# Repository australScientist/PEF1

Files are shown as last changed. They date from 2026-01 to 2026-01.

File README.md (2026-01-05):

# The Ecophysiometer: An Open-Source Multipurpose Environmental Sensor

The **Ecophysiometer** is a low-cost (\~US\$128), modular environmental monitoring platform designed to acquire rich optical data and interpret it through chemometric calibration. Developed at the Universidad Nacional de Córdoba (UNC), CONICET and the Technical University of Rheinland-Pfalz, Landau (RPTU) this project shifts analytical complexity from hardware to software, enabling multi-analyte quantification with flexible, 3D-printable instrumentation.

## 📁 Repository Structure

The project is organized to support both hardware fabrication and data analysis:

```         
/Design/Hardware: Engineering files for the flow cell, modular housing, and sensor mounts in FreeCAD and STL formats. Includes KiCAD project files for the constant-current PCB.
```

/Design/Software: Python source code including the core Measurement.py, ImageProcessor.py, and SpectralData.py layers .

/Instructions: Step-by-step assembly guides, including the critical IR filter removal tutorial for the Raspberry Pi Camera .

/Characterisation: Raw data and R scripts used to validate signal stability, linear range, and manufacturing variability.

/Implementation examples: Datasets and R models for the primary use cases: Turbidity and Phytoplankton differential quantification.

## 🛠️ Key Technical Features

```         
Software-Defined Specificity: Analyte detection is determined by chemometric calibration (PLSR, PCA) rather than fixed hardware filters.
```

High-Certainty Signal Processing: The pipeline aligns 450 vertical rows and applies 5-pixel binning, deriving each data point from the average of 2,250 measurements to maximize the signal-to-noise ratio .

Reproducible Hardware: Designed for manufacturing with minimal technical knowledge using locally available electronic materials and 3D printing in PETG .

## 🚀 Getting Started

### 1. Hardware Fabrication

```         
3D Printing: Print parts found in /Design/Hardware. Black PETG is recommended to minimize internal reflections.
```

[Circuitry]{.underline}: Fabricate the PCB using the provided KiCAD files or the CNC-ready .nc files in the Circuit Board directory.

[Sensor Modification]{.underline}: Follow Instructions/IR_REMOVAL.md to remove the IR cut-off filter from the Raspberry Pi Camera V1.3.

### 2. Software Installation

Clone this repository and install the dependencies: Bash

git clone <https://github.com/australScientist/PEF1.git> cd PEF1 pip install -r Design/Software/PEF0/requirements.txt

### 3. Basic Operation

[Calibration]{.underline}: Run test.py to identify the linear integration time for your specific hardware assembly .

[Measurement]{.underline}: Launch the graphical interface: Bash

```         
python3 Design/Software/PEF0/src/GUI2.py
```

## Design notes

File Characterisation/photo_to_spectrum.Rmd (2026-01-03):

---
title: "photo_to_spectrum"
author: "Guido Marconi"
date: "`r Sys.Date()`"
output: html_document
---

```{r Rsetup, include=FALSE}
knitr::opts_chunk$set(echo = TRUE)
library(reticulate)
renv::use_python()
library(tidyverse)
library(gganimate)
```

```{python PySetup, include=FALSE}
#import matplotlib as mpl
import numpy as np
#import matplotlib.pyplot as plt
from scipy.signal import correlate
import rawpy
import os
```

## Intro

The goal of the instrument is to measure light intensities at different wavelengths. To achieve this two simple concepts are used. The first is that diffraction can be used to produce a spatial separation of light into its spectral components. The second is that the intensity of each component of light can be then recovered by an array of sensors with capacity for spatial resolution, such as a camera. The problem begins with the oversimplification of considering cameras just as an array of sensors and continues with a fundamental misconseption about what their design goals were. Cameras are devices designed to capture images that are comparable to the human visual system. As trivial as this statement seems, it contains the information needed to structure the process of adapting a camera to suit our goal. 

Fundamentally the root cause of the problem to be solved is that light as perceived by humans is not exactly the same as light as physical phenomenon. Humans experiment light as colour, and cameras (and the post-post processing of the photos) aim at replicating this perceptual phenomenon. Thus, a photograph is composed of patterns of colour at different points of space, not "just light".

Briefly, colour is a physiological response to light and, according to the CIE 1931, its the product of the stimulation of three types of cone cells. This gives rise to the idea of colour as a response to tristimulus values and to the representation of colour as a space defined by three axis. Perhaps the most intuitive representation of this is the RGB colour space defined by the amount of light at each of Red, Green and Blue "primary" colours. A generalization of this is that colour, as perceived by humans, can be decomposed into three parts parts: one regarding the illuminance of the colour and the remaining two describing its chrominance. Making this distinction is important because, for analytical purposes, the illuminance aspect of the signal is the only relevant component but when the signal is recovered from the camera it is convoluted with all the other aspects that make the image have colour.

Leaving behind all the optical elements, cameras can be thought as having two components. A sensitive component aimed at measuring the illuminance part of colour and another part aimed at obtaining chromatic information. Briefly, the sensors translate photon counts into a voltage difference that gets amplified and red. The working principle is the photoelectric effect. Basically, pixels work as capacitors that hold charge generated when photons excite electrons until they it is red, resetting the pixel for the next measurement. This is enough to represent the luminance aspect of colour, but not the chrominance. To overcome this and produce a tricromatic image, each pixel in the sensor is coated with a filter for red, green and blue light, conforming a colour filters array (CFA). This CFA restricts each pixel to capture information only about the intensity of light that was not absorbed by the filter on top of it. Thus the pixel values in the raw image represent the amount of light only in one primary component of light (either blue, green or red). 

To solve this issue post processing of the image interpolates the values of the remaining components to achieve a full colour representation of each pixel. There are several interpolation algorithms that can be used, each with its advantages and disadvantages and will be analized in a future section. Another situation to take into account is that human perception of brightness is not linear, it follows a power function. To emulate this, comonly post processing uses a gamma correction that translates the quasi linear response of the instrument into a power distribution. Lastly, when the luminance component is obtained from the full colour value of each pixel, it is usually a ponderated sum of the R, G and B components taking into account our sensitivity to each of these colours. 

Here we face the first set of problems or warnings that need to be addressed:

- Filters restrict the amount of photons that get sensed to three bandwidths. This has two practical implications:

  - The measurement of the luminance is composed from the the true colour representation of each pixel, which in turn is an interpolation from the observed RGB values.
  
  - There is a limitation in the bandwidth.

- The mechanism used to obtain the chrominance components of the colour is rooted into the spatial disposition of pixels. This is something to take into account because the spectra is already spatially separated.

- The gamma correction has to be set as a power of one and with a slope of one so that the response in the R, G and B components is linear.

- A gray-scale or luminance is a pondered average of RGB components such that the result represents 

The camera is based on the OmniVision [OV5647 sensor]("https://cdn.sparkfun.com/datasheets/Dev/RaspberryPi/ov5647_full.pdf"). It is a CMOS an sensor array of 2624 columns to 1965 rows, with a pixel dimension of 1.4 µm × 1.4 µm and a total sensor area of 3.76 × 2.74 mm.

## Working with the Raw image

### Script to process the photo

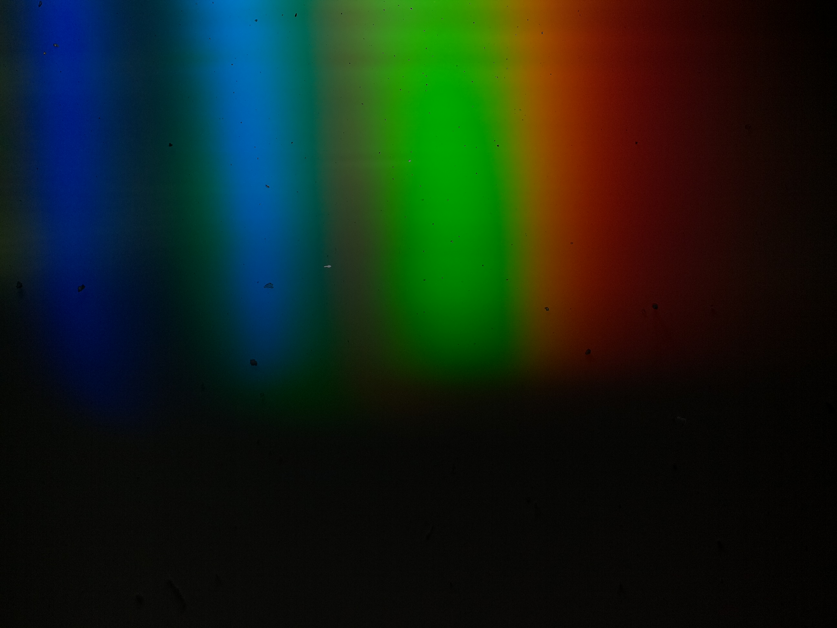
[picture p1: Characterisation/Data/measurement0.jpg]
Raw output Sensor output
Concretely, the output of the camera looks something like this: . Visual inspection already allow us to identify some behaviours that should reflect on the final result (spectra):

+ The shortest wavelengths (blue) of the spectra are present at the left part of the picture while the longer wavelengths (red) are at the rightmost part.

+ The intensity of the spectra is not uniform. It has bands of higher and valleys of lower intensity.

+ The lowest part of the picture is black. This could be used to calculate the signal to noise ratio of the individual wavelengths.

This is a processed image for the purpose of showing the output. The raw image is processed with the postprocess function in the rawpy package. The gamma correction (parameter gamma) was seted to a power of one and a slope of one to avoid compression and hence improove linearity in the response. The demosaicing algorithm used was DHT proposed by Ddubois because it showed small error in [Losson O. et al 2010](https://hal.archives-ouvertes.fr/hal-00683233/document).

```{python}
raw = rawpy.imread('./Data/measurement0.dng')
rgb = raw.postprocess(demosaic_algorithm=rawpy.DemosaicAlgorithm(11),gamma=(1,1), no_auto_bright=True, output_bps=16)

```

### Exploring the sensor's output

After demosaicing a 1944x2592x3 tensor or array is obtained. in this array, each pixel's position is represented by the first two components while the third informs if the value corresponds to the red, green or blue component of colour. To keep in mind, the columns represent the variation in the horizontal direction, encompasing the spectral variation. The rows represent replicate measurements of that same spectrum. 

#### Column behaviour

The first goal is to explore the behaviour of column pixels to see if the RGB components of colour exhibit the expected behaviour. That is, there is a peak at the blue component at the left most pixels where the blue part of the spectrum hit, green at the center and red at the rightmost part as can bee seen at the photo photo of the spectra Sensor output.

```{r}
RGB = py$rgb
RedC = RGB[,,1]
GreenC = RGB[,,2]
BlueC = RGB[,,3]
colnames(RedC) = 1:ncol(RedC)
colnames(GreenC) = 1:ncol(GreenC)
colnames(BlueC) = 1:ncol(BlueC)
RedC = RedC %>% as_tibble()
GreenC = GreenC %>% as_tibble()
BlueC = BlueC %>% as_tibble()
RedC$hpix = 1:nrow(RedC)
GreenC$hpix = 1:nrow(GreenC)
BlueC$hpix = 1:nrow(BlueC)
RedC$Channel = "red"
GreenC$Channel = "green"
BlueC$Channel = "blue"
all = bind_rows(BlueC,RedC,GreenC)
allGathered = all %>% gather(key = "vpix","value",1:(ncol(all)-2))
allGathered$hpix = allGathered$hpix %>% as.numeric()
allGathered$vpix = allGathered$vpix %>% as.numeric()
allGathered$colour = ifelse(allGathered$Channel == "blue", "#0c79f5",ifelse(allGathered$Channel == "green","#5bb03f","#f04f05"))
ggplot(allGathered %>% filter(hpix == 1),aes(vpix,value,colour = Channel)) + geom_line() + scale_color_manual(values=c("blue","green","red"))
```
This graph shows that the filters do exhibit the peaks at the position that were expected. However, the display of the individual row of pixels also displays a high level of noise that will have to be delt with in the future. 

#### Row Behaviour

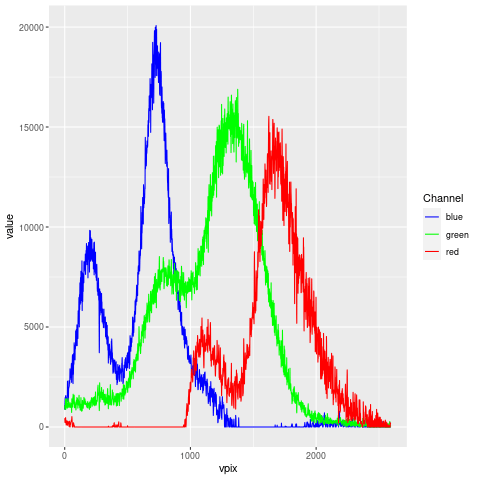
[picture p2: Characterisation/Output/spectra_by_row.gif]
Now, regarding the row behaviour, it can be seen that conformly the pixel row descends the intensity recorded at each pixel drops  . Another thing that becomes evident is that there is a pixel shift that is correlated with the pixel row. This may be due to a manufacturing limitation at the time of sticking the difraction grating.

```{r eval=FALSE, include=FALSE}
spInRow = ggplot(allGathered %>% filter(hpix == seq(1,1944, by =  9)),aes(vpix,value,colour = Channel)) + geom_line() + scale_color_manual(values=c("blue","green","red")) + transition_states(hpix)
anim_save("spectra_by_row.gif",spInRow)
```

### Signal treatment

The signal informed by each pixel is a random variable whose value is conditional on the amount of photons that inside on it and their wavelength. Since the measurement made by each pixel is a random event it has an associated variance that we interpret as noise. Because of the designed physical setup, the horizontal position (pixel column) is a proxy of wavelength and the vertical position (pixel row) represent just replicate measurements once the shift has been accounted for. This means that, within a certain range, pixels at a same column can be thought as a sample of a population. If we face the measurement in this framework we work with the mean of the sample instead of individual values. This has two advantages. The first is that can use the Law of Large Numbers to ensure that the value informed by the instrument will tend to the population mean. This limit behaviour is reasuring in the sense that, despite unknown, the value informed by the instrument will tend to a "true value". Also, since the Estandard Error is a function that decreases with the square root of the sample size, the estimation of the sample mean will get more accurate with increased sample size. The other advantage is derived from the Central Limit Theorem. The distribution of expected values is guaranteed to converge to a normal distribution at infinite sample size. This eases the use of more standard models.

The first thing to do before anything is to combine all the signals corresponding to the three channels to obtain a total signal. The next step is to obtain an approximate pixel row where the pixels start decaying and which parts are somewhat similar. To do this the sum of all pixel values at the same row was obtain as a sumary value.

```{r}
Signal = RGB[,,1] + RGB[,,2] + RGB[,,3]
totalSignal = tibble("horizontalPix" = 1:nrow(Signal), "value" = rowSums(Signal))
totalSignal %>% ggplot(aes(horizontalPix,value)) + geom_line()
```
As can be seen, the signal starts decaying strongly around the pixel row number 500. To test how does the average and the standard deviation of the signal behaves as the sample size increases we built a series whose results are plotted below.

```{r}
MEAN = vector(length=50)
SD = vector(length=50)
for(i in 0:49){
  MEAN[i] = Signal[1:(i*38+2),] %>% rowSums() %>% mean()
  SD[i] = Signal[1:(i*38+2),] %>% rowSums() %>% sd()
}
SignalPixelSum = tibble("RowMean" = MEAN,"RowSD" = SD, "RowCV" = SD/MEAN,"RowNumber" = (0:49*38+2))
ggplot(SignalPixelSum,aes(x=RowNumber)) + geom_point(aes(y=RowMean)) + geom_point(aes(y=RowSD))  + scale_y_continuous(name = "Mean",sec.axis = sec_axis( trans=~., name="Standard Deviation"))
```
As expected, the mean and the standard deviation remains stable until the 500th pixel. Once this threshold is surpassed the mean starts to decay (dragged by the lower signal) and the standard deviation increases. To apply the CLT and the LLN it is important that random variables are somewhat independent and identically distributed. For practical reasons, if they have similar means and standard deviations will be enough. To test up to which pixel they behave somewhat as required we can check the above pixels and use coefficient of variation to assess where does the change starts to occur. 

```{r}
ggplot(SignalPixelSum,aes(RowNumber,RowCV)) + xlab("Number of rows used") + geom_point()
```
From this we can see that sampling the first 450 pixels is a conservative but sufficient sample size.

#### Aligning the spectra

Before adding up the columns of the first 250 rows care has to be taken about the phase shift to prevent loosing spectral resolution. To do this, the cross correlation between every spectrum against the first will be used to obtain the shift between the signals and then subtract it. 

```{python }

def get_pixel_shift(A, B):
    # regularize datasets by subtracting mean and dividing by s.d.
    A = A - A.mean()
    A = A / A.std()
    B = B - B.mean()
    B = B / B.std()
    xcorr = correlate(A, B)
    # delta time array to match xcorr
    nsamples = A.size
    dt = np.arange(1 - nsamples, nsamples)
    recovered_time_shift = dt[xcorr.argmax()]
    return (recovered_time_shift)
def align_spectra(F):
    size = len(F[:, 0])
    Out = F[:, :]  # select first row
    A = F[0, :]  # select first row
    for i in range(1, size):  # and then iterate through the rest, comparing against the first
        B = F[i, :]
        shift = get_pixel_shift(B, A)
        #print(shift)
        # calculates the lag between both rows
        Out[i, :] = np.roll(F[i, :],-shift)  # then shifts the row to match both spectra, replacing the spectrum in the original data
    return (Out)
Aligned = align_spectra(np.array(r.Signal[0:450,]))
```

```{r eval=FALSE, include=FALSE}
NoShift = Signal[1:250,]
colnames(NoShift) = 1:ncol(NoShift)
NoShift = NoShift %>% as_tibble()
NoShift$hpix = 1:250
NoShift = NoShift %>% gather("vpix","value",1:2592)
NoShift$vpix = NoShift$vpix %>% as.numeric()
ggplot(NoShift[NoShift$hpix %in% seq(1,250,by = 2),],aes(vpix,value)) + geom_line() + transition_states(hpix)
anim_save("NoShift.gif")

```

```{r eval=FALSE, include=FALSE}
Shifted = py$Aligned
colnames(Shifted) = 1:ncol(Shifted)
Shifted = Shifted %>% as_tibble()
Shifted$hpix = 1:450
Shifted = Shifted %>% gather("vpix","value",1:2592)
Shifted$vpix = Shifted$vpix %>% as.numeric()
ggplot(Shifted[Shifted$hpix %in% seq(1,250,by = 2),],aes(vpix,value)) + geom_line() + transition_states(hpix)
anim_save("Shifted.gif")
```

The alignment results in a slight improvement of the pixel shift. The effect is small because all shift with respect to the first row was less than 30 pixels in all cases.
Here are the not aligned spectra 

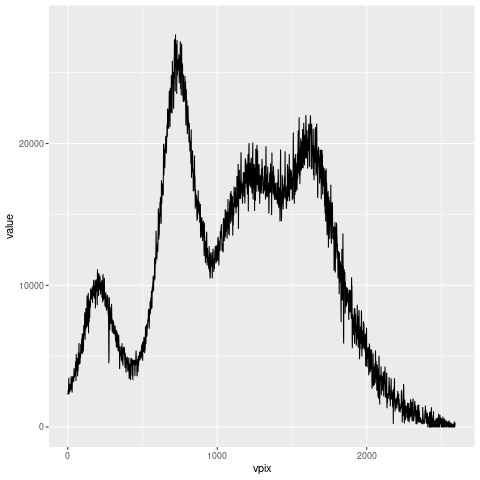
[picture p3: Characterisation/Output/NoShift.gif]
.

And the aligned spectra

Plot Rows.

#### Averaging 

The next thing we have to deal with is the artifact that appears at the last pixels, due to the alignment process. The easiest solution is to chop those last 30 pixels. In practice i will eliminate the first 32 pixels because 2560 has more factors than 2562.

```{r}
rm(Shifted,NoShift)
Aligned = py$Aligned
SpectrumMean =colSums(Aligned)
SpectrumSD = apply(Aligned,2,sd)
SpectrumMean %>% plot(type="l")
SpectrumMean = SpectrumMean[0:2560]
SpectrumMean %>% plot(type="l")

```
Another thing to do to improve the signal and reduce its noise is to group pixel and average them. Since there are 2560 pixels encompassing an designed spectral range of 500 nm (from 350 to 850) the theoretical pixel resolution is a little less than 0.2 nm. However, it is really improbable that hat the real spectral resolution of this instrument is less than a nm. This means that the spectrum is oversampled, and this can be used at our advantage. Assuming an optimistic resolution of 1 nm, this means that there are around 5 pixels per nm that can be grouped to estimate the true value of light intensity for the $\delta\ 1 nm. 
 
```{R }
SpectrumMean = SpectrumMean %>% matrix(nrow = 5) %>% colMeans()
SpectrumMean %>% plot(type="l")
```
#### Code

The programming language that will be used to handle the instrument will be python, because it has many libraries by default. According to the results I've presented code responsible for transforming the photo into a spectra will be the following. 
``` {python}
import numpy as np
from scipy.signal import correlate
import rawpy
#from numpy import savetxt
import os

def get_pixel_shift(A, B):
    # regularize datasets by subtracting mean and dividing by s.d.
    A = A - A.mean()
    A = A / A.std()
    B = B - B.mean()
    B = B / B.std()
    xcorr = correlate(A, B)
    # delta time array to match xcorr
    nsamples = A.size
    dt = np.arange(1 - nsamples, nsamples)
    recovered_time_shift = dt[xcorr.argmax()]
    return (recovered_time_shift)
def align_spectra(F):
    size = len(F[:, 0])
    Out = F[:, :]  # select first row
    A = F[0, :]  # select first row
    for i in range(1, size):  # and then iterate through the rest, comparing against the first
        B = F[i, :]
        shift = get_pixel_shift(B, A)
        # calculates the lag between both rows
        Out[i, :] = np.roll(F[i, :],-shift)  # then shifts the row to match both spectra, replacing the spectrum in the original data
    return (Out)

def get_spectrum(pathToPhoto):
    raw = rawpy.imread(pathToPhoto)
    rgb = raw.postprocess(demosaic_algorithm=0,gamma=(1,1), no_auto_bright=True, output_bps=16)
    Signal = rgb[0:450,:,0]+rgb[0:450,:,1]+rgb[0:450,:,2]
    Aligned = align_spectra(Signal)
    SpectrumFull = np.mean(Aligned[:,0:2560],axis=0)
    test = np.reshape(SpectrumFull,(512,5))
    Spectrum = np.mean(test,axis=1)
    return(Spectrum)
```
#### Accounting for the noise

There are many pixels at the bottom of the spectrum that are apparently not illuminated and can be used to calculate signal to noise ratio. As could be seen above, rows 1500 to 1944 do not display significant signal. Columns 1 to 2560 will be kept and then blocks of contiguous 5 pixels will be averaged, simmilarly to the data treatment described above. The first thing to do is to see if the signal has some pattern, to perform some sort of baseline correction on the signal. As can be seen there is a small baseline, but doesn't change that much when is substracted from the original signal.

```{r eval=FALSE, include=FALSE}
Noise = (RGB[1500:1944,1:2560,1]+RGB[1500:1944,1:2560,2]+RGB[1500:1944,1:2560,3]) %>% apply(1,function(x) {matrix(x,byrow = T,ncol = 5) %>% rowMeans()}) %>% t()

Noise %>% colMeans() %>% plot()
sdNoise %>% plot()
par(mfrow=c(2,1))
(SpectrumMean-colMeans(Noise)) %>% plot(type="l")
plot(SpectrumMean,type="l")
plot(Noise %>% colMeans(),sdNoise)
par(mfrow=c(1,1))
Noise %>% colMeans() %>% plot()
```

Analysing the standard deviation of the uniluminated pixels allow to study the variation due to noise. The standard deviation presents a dependence with the pixel intensity as showd below

```{r eval=FALSE, include=FALSE}
sdNoise = Noise %>% apply(2,sd)
par(mfrow=c(2,1))
plot(sdNoise)
plot(Noise %>% colMeans(),sdNoise)
par(mfrow=c(1,1))
```

Finaly, signal to noise ratio can be calculated as the quotient of the mean signal with the standard deviation of the noise:

```{r eval=FALSE, include=FALSE}
SNR = SpectrumMean/sdNoise
plot(SNR)
```

#### Denoising

To proceed with the denoising two alternatives will be assessed. The first is to use the Fourier transform to filter frequencies of variation that are associated with noise. The principle behind this technique is that singals can be thought as functions mapping from one domain into another. In this case, the signal is a function that assigns a particular intensity for each pixel. Thus, the signal is in the pixel domain. However, the signal can be also decomposed into a sum of sine and cosines (those provide the shift) with different frequencies (a spatial frequency in this case). This allow us to obtain the frequency domain of the signal. We can think of this representation of the function as assigning each frequency with an intensity. As can be seen by the plots, our spectrum has a distinguishable shape that is distorted by a minor amount of variation. Thus, it is expected that the "intensities" of the frequency components  corresponding to to non-noise to be greater than frequencies corresponding to noise. So, what can be done is to find a threshold corresponding to noise. To do this, the power spectrum is obtain by multipliying the FFT of the spectrum with its complex conjugate to retain only the real part.

```{r eval=FALSE, include=FALSE}
fftAveraged = fft(SpectrumMean)
PowerSpectrum = (fftAveraged*Conj(fftAveraged)/length(fftAveraged)) %>% Re()  
PowerSpectrum %>% sort(decreasing = TRUE) %>% log10() %>% plot(type="l")

SpectrumMean %>% plot()
py$denoise_fourie(SpectrumMean,1e12)[[1]] %>% Re() %>% plot(type="l")

Power =  c(1e16,1e15,1e14,1e13,1e12,1e11,1e10)

Denoise_fft = function(TH,data){
  fftAveraged = fft(data)
  PowerSpectrum = (fftAveraged*Conj(fftAveraged)/length(fftAveraged)) %>% Re()
  Index = PowerSpectrum > TH
  filtered = (Index*fftAveraged) %>% fft(inverse = TRUE) %>% Re()
  return(filtered)
  
}
par(mfrow=c(7,1))
map(Power,Denoise_fft,data = SpectrumMean) %>% map(plot,type = "l")
map(seq(1e11,1e12,100),Denoise_fft,data = SpectrumMean) %>% map(plot,type = "l")
map(c(1e11,2e11,3e11,4e11,5e11,6e11,7e11,8e11,9e11,1e12),Denoise_fft,data = SpectrumMean) %>% map(plot,type = "l")

(PowerSpectrum >1e12) %>% plot()
(PowerSpectrum >1e12) %>% which()

Denoise_fft_fixed = function(data){
  fftAveraged = fft(data)
  Index = rep(FALSE,2560)
  Index[1:10] = !Index[1:10]
  Index[2552:2560] = !Index[2552:2560]
  filtered = (Index*fftAveraged) %>% fft(inverse = TRUE) %>% Re()
  return(filtered)
  
}
Denoise_fft_fixed(SpectrumMean) %>% plot(type="l")

map(c(1e16,1e15,1e14,1e13,1e12,1e11,1e10),py$denoise_fourie(SpectrumMean,.))
par(mfrow=c(1,1))
PowerSpectrum >1e
```

### Noise Characterization

```{R eval=FALSE, include=FALSE}
Noise = Signal[1500:1700,1:2560] %>%  colSums()
plot(Noise,type="l")
fftAveraged = fft(Noise)
PowerSpectrum = (fftAveraged*Conj(fftAveraged)/length(fftAveraged)) %>% Re()  
PowerSpectrum %>% plot(type="l")
(SpectrumMean-Noise) %>% plot(type="l")
Signal[1500:1700,1:2560] %>% unlist() %>% shapiro.test() %>% .[["p.value"]] %>% plot(type="l")
```

```{python eval=FALSE, include=FALSE}
def denoise_fourie(data,TH):
    #suma = (rgb[index,:,0] + rgb[index,:,1] + rgb[index,:,2])/3
    n = len(data)
    fhat = np.fft.fft(data,n)
    psd = fhat * np.conj(fhat)/n
    freq = (1/(n)) * np.arange(n)
    
    threshold = TH
    psd_idxs = psd > threshold #array of 0 and 1
    psd_clean = psd * psd_idxs #zero out all the unnecessary powers
    fhat_clean = psd_idxs * fhat #used to retrieve the signal
    signal_filtered = np.fft.ifft(fhat_clean) #inverse fourier transform
    return(signal_filtered, abs(psd))
```

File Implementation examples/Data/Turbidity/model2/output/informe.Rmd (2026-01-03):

---
title: "Método Turbidez"
author: "Guido Marconi"
date: "`r Sys.Date()`"
output: pdf_document
---

```{r setup, include=FALSE}
knitr::opts_chunk$set(echo = TRUE)
library(jsonlite)
library(tidyverse)
library(pls)
library(caret)
library(gridExtra)

read_spectra = function(path){
  File = read_json( path)
  
  TurbiSpectra = map(File,function(x){x %>% .[["spectrum"]] %>% unlist()}) %>% bind_cols() %>% t() %>% as_tibble()
  ID = map(File,function(x){x %>% .[["tag"]] %>% strsplit("-") %>% unlist()}) %>% bind_cols() %>% t() %>% as_tibble()
  SiD = map(File,function(x){x %>% .[["ID"]] %>% unlist()}) %>% bind_cols() %>% t() %>% as_tibble()
  
  colnames(TurbiSpectra) = 1:512
  colnames(ID) = c("NTU","LED")
  TurbiSpectra = bind_cols(TurbiSpectra,ID) 
  TurbiSpectra$ID = SiD$V1  
  return(TurbiSpectra)
}

calibration = read_spectra("../data/Curva.json")
test = read_spectra("../data/TEST.json")
calibration2 = read_spectra(path = "../data/CurvaDef.json")
blanco = read_spectra("../data/Blanco.json")
colnames(blanco)[1:512] = paste0("p",1:512)

colnames(calibration)[1:512] = paste0("p",1:512)
colnames(calibration2)[1:512] = paste0("p",1:512)
colnames(test)[1:512] = paste0("p",1:512)

AllData = bind_rows(calibration,calibration2,test)
AllData$NTU = AllData$NTU %>% as.numeric()
AllData = AllData %>% select(-ID)

AllData = AllData %>% filter(NTU <501,NTU >19)
allTidy = AllData %>% group_by(LED) %>% nest()
allTidy$data = allTidy$data %>% map(function (x) {x[-c(1,3,29:38),]})

```

# Desarrollo de método de medición de turbidez con el Ecofisiómetro

## Reseña:
La turbidez es una expresión de la propiedad óptica  que causa la dispersión y absorción de la luz, en lugar de su transmisión, al mantener la dirección y flujo lumínico constante a través de la muestra. La turbidez en el agua está causada por materia suspendida y coloidal, pudiendo ser de origen inorgánico (arcillas, limo, cenizas, etc) u orgánico (materia orgánica particulada, células en suspensión, etc.). Como unidad de medición de turbidez se utiliza a las "Unidades Nephelometricas de Turbidez" (NTU), por sobre las tradicionales Unidades de Turbidez de Jackson (JTU), por su menor sensibilidad a cambios instrumentales.

## Metodología:

Para evitar discrepancias en el tipo de material particulado empleado para calibrar métodos turbidimétricos, se utilizará el estandar primario de polímero de formazina, propuesto en la metodología standard APHA 23-2130 (2017)$^{1}$ .

Brevemente, un primer experimento fue llevado a cabo para determinar los rangos operativos del método de calibración. Con estos fines, se hizo una curva de calibración que comprendía un rango entre 0 y 1000 NTU. Admás se realizaron 20 mediciones del blanco (agua calidad mili-q) para estimar un límite de cuantificación.

Una vez establecidos los límites de cuantificación, y teniendo en cuenta que el objetivo es trabajar con muestras de aguas residuales, se procedió a generar un pull de calibración comprendido en el rango de 20 a 500 NTU. Este consistió de 32 soluciones preparadas a lo largo de  dos semanas. Se procedió a realizar un análisis exploratorio de datos para seleccionar las zonas del espectro más correlacionadas con la variable respuesta. Dicho análisis fue gráfico y mediante análisis de componentes principales.

Se entrenaron una serie de modelos, probando su desempeño usando sumbuestreo aleatorio repetido. Se utilizó debido a que la segmentación en conjunto de testeo y calibración no se encuentra recomendada para menos de 40 datos $^{2}$. Se utilizaron 8 muestras para testear el desempeño del modelo, estimando el modelo con 26 muestras. Se realizaron 200 repeticiones para estimar el error absoluto medio de cada modelo.

## Resultados:

Aquí sólo se incluye la documentación referida al modelo final seleccionado, luego de la exploración de potenciales candidatos resultantes de aplicar una metodología similar utilizando distintas fuentes de iluminación y tratamiento de los datos. 

### Análisis exploratorio

Los espectros de la luz dispersada, resultantes de iluminar las muestras con el led con máximo de emisión a 660 nm (fig. 1), y el biplot (fig. 3) no evidencian datos atípicos con lo que se procederá a utilizar todo los datos. Las variables que más varianza en la base de datos generan pueden verse el gráfico de loadings (fig. 2) para cada pixel, en el primer componente principal. Al comparar la fig 2 y la 1 puede verse que las variables que los píxeles que más varianza explican son aquellos que coinciden con los picos del espectro, por lo que se eligió un punto cercano al máximo de emisión (pixel 150). La señal medida por el pixel 431 en función de la turbidez (fig. 4) muestra una tendencia a incrementar con la turbidez linealmente.

```{r echo=FALSE,fig.cap="Espectros obtenidos al iluminar la muestra con el LED de 660 nm"}
allTidy$Gathered = allTidy$data %>%map(function(x){gather(x,pixel,value,1:512) %>% mutate(pixel = pixel %>% str_extract("\\d+") %>% as.numeric())})
allTidy$Gathered = allTidy$Gathered %>% map(function(x){x %>% mutate(NTU = NTU %>% as_factor) })

allTidy$spectralPlots = map(allTidy$Gathered,function(x){ggplot(x,aes(pixel,value,colour = NTU)) + geom_point(size = 0.1) + ylab("Intensidad (UA)")})
allTidy$spectralPlots[[1]] = allTidy$spectralPlots[[1]] + ggtitle("Transmitancia")
allTidy$spectralPlots[[2]] = allTidy$spectralPlots[[2]] + ggtitle("Scattering 365nm")
allTidy$spectralPlots[[3]] = allTidy$spectralPlots[[3]] + ggtitle("Scattering 395nm")
allTidy$spectralPlots[[4]] = allTidy$spectralPlots[[4]] + ggtitle("Scattering 440nm")
allTidy$spectralPlots[[5]] = allTidy$spectralPlots[[5]] + ggtitle("Scattering 470nm")
allTidy$spectralPlots[[6]] = allTidy$spectralPlots[[6]] + ggtitle("Scattering 530nm")
allTidy$spectralPlots[[7]] = allTidy$spectralPlots[[7]] + ggtitle("Scattering 600nm")
allTidy$spectralPlots[[8]] = allTidy$spectralPlots[[8]] + ggtitle("Scattering 660nm")

allTidy$spectralPlots[[8]]
allTidy$PCA = allTidy$data %>% map(function(x){x[1:512] %>% prcomp(scale = F)})
```

```{r echo=FALSE, fig.cap="Loadings del primer componente principal, explicando el 93,97% de la varianza en el conjunto datos, indicando los píxeles que más aportan a la varianza de la base de datos"}
allTidy$PCA[[8]]$rotation[,1] %>% plot(main = "loadings PC1 (93.97%)")
```

```{r echo=FALSE,fig.cap="Biplot de los primeros dos componentes, mostrando ordenamiento de los datos tras la reducción dimensional"}
allTidy$PCA[[8]] %>% biplot(var.axes = F,main = "PC1 vs PC2")
```

```{r echo=FALSE,fig.cap="Respuesta del equipo, en el pixel seleccionado, a distintos niveles de turbidez"}
ggplot(allTidy$data[[8]],aes(NTU,p431)) + geom_point() + ylab("señal (UA)")
```

### Desarrollo del modelo

El modelo con mejor ajuste resultó ser un modelo lineal simple, ajustado con OLS. $$NTU = \beta_{0} + \beta_{1}S_{p431} + \epsilon$$ 

#### Validez

El modelo seleccionado no presenta patrones en los observables en el gráfico de residuos vs predichos, corroborando el supuesto de independencia. El supuesto de homocedasticidad se verifica al inspeccionar el gráfico de residuos vs predichos y tras realizar al prueba de Goldfeld-Quandt ($pval_{gq} = 0.2$). La tabla ANOVA muestra que el modelo y sus términos son estadísiticamente significativos. La validez del supuesto de normalidad de los residuos no se cumple al rechazar la hipótesis nula de normalidad del test de shapiro wilks ($pval_{shapiro wilks} = 0.008$) ni mediante la inspección gráfica del QQplot.

```{r echo=FALSE,fig.cap="Tabla de ANOVA del modelo"}
Control = caret::trainControl(method = "repeatedcv",repeats = 200,number = 8)
modelo = caret::train(NTU ~ p431 ,
                    data = allTidy$data[[8]],
                    method = "lm",trControl = Control)
modelo$finalModel %>% summary# %>% knitr::kable()

```

```{r echo=FALSE,fig.cap="Gráfico de control"}
par(mfrow=c(2,2))
plot(modelo$finalModel)
```

#### Performance

El modelo seleccionado presenta un error medio absoluto de 11.56 NTU lo que representa un error medio del 7.8%. El promedio de predicciones de concentración tras medir blancos (n = 16) resultó de 18.36 NTU y el desvío estándar de 1.66, por lo que el límite de detección de la técnica se estima en 23.33 NTU.

```{r echo=FALSE,fig.cap="performance de todos los modelos"}
modelo$results %>% mutate("errorPorcentualMedio" = (MAE/mean(allTidy$data[[4]]$NTU)*100)) %>% select(RMSE,MAE,Rsquared,errorPorcentualMedio) %>% knitr::kable(align = "c")
```

## Discusión:

Los resultados muestran que el ecofisiómetro pudo ser calibrado para medir turbidez entre a 23.33 NTU y 500 NTU con un error absoluto promedio de 11.56 NTU, utilizando el siguiente modelo estadístico.  $$\hat{NTU} = 5.54 + 0.12S_{p431}$$ Trabajos previos $^{3}$ han reportado que los valores de turbidez encontrados en aguas residuales afluentes ronda las $201 \pm 114 NTU$. Esto hace al rango operativo de la curva adecuado a los fines de este estudio, puesto que puede resultaría útil en aproximadamente el 94% de los casos. Al encontrarse el promedio de la curva de calibración (148.28 NTU) cerca de la media ambienta, es esperable que el error porcentual de predicción sea menor. A pesar que se viola el supuesto de normalidad, se considera que los modelos lineales ajustados con OLS son robustos ante falta de normalidad.

## Conclusión

Se pudo calibrar un modelo para estimar la turbidez en unidades neftelométricas, acorde a las necesidades del trabajo a realizarse.

## Bibliografía

1 - Baird, R.B. et al. (2017) “2130 - turbidity,” in Standard methods for the examination of water and wastewater. 23rd edn. New York: American Public Health Association. 

2 - Peris-Díaz, M.D. and Krężel, A. (2021) “A guide to good practice in chemometric methods for vibrational spectroscopy, electrochemistry, and hyphenated Mass Spectrometry,” TrAC Trends in Analytical Chemistry, 135, p. 116157. Available at: https://doi.org/10.1016/j.trac.2020.116157. 

3 - Guedes-Alonso, R. et al. (2020) “Pharmaceutical and personal care product residues in a macrophyte pond-constructed wetland treating wastewater from a university campus: Presence, removal and ecological risk assessment,” Science of The Total Environment, 703, p. 135596. Available at: https://doi.org/10.1016/j.scitotenv.2019.135596.

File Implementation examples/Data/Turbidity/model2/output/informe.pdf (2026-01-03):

## Método Turbidez

Guido Marconi

2023-05-04

## Desarrollo de método de medición de turbidez con el Ecofisiómetro

Reseña:

La turbidez es una expresión de la propiedad óptica que causa la dispersión y absorción de la luz, en lugar de su transmisión, al mantener la dirección y flujo lumínico constante a través de la muestra. La turbidez en el agua está causada por materia suspendida y coloidal, pudiendo ser de origen inorgánico (arcillas, limo, cenizas, etc) u orgánico (materia orgánica particulada, células en suspensión, etc.). Como unidad de medición de turbidez se utiliza a las “Unidades Nephelometricas de Turbidez” (NTU), por sobre las tradicionales Unidades de Turbidez de Jackson (JTU), por su menor sensibilidad a cambios instrumentales.

Metodología:

Para evitar discrepancias en el tipo de material particulado empleado para calibrar métodos turbidimétricos, se utilizará el estandar primario de polímero de formazina, propuesto en la metodología standard APHA 23-2130 (2017)¹

Brevemente, un primer experimento fue llevado a cabo para determinar los rangos operativos del método de calibración. Con estos fines, se hizo una curva de calibración que comprendía un rango entre 0 y 1000 NTU. Admás se realizaron 20 mediciones del blanco (agua calidad mili-q) para estimar un límite de cuantificación.

Una vez establecidos los límites de cuantificación, y teniendo en cuenta que el objetivo es trabajar con muestras de aguas residuales, se procedió a generar un pull de calibración comprendido en el rango de 20 a 500 NTU. Este consistió de 32 soluciones preparadas a lo largo de dos semanas. Se procedió a realizar un análisis exploratorio de datos para seleccionar las zonas del espectro más correlacionadas con la variable respuesta. Dicho análisis fue gráfico y mediante análisis de componentes principales.

Se entrenaron una serie de modelos, probando su desempeño usando sumbuestreo aleatorio repetido. Se utilizó debido a que la segmentación en conjunto de testeo y calibración no se encuentra recomendada para menos de 40 datos 2
. Se utilizaron 8 muestras para testear el desempeño del modelo, estimando el modelo con 26 muestras. Se realizaron 200 repeticiones para estimar el error absoluto medio de cada modelo.

Resultados:

Aquí sólo se incluye la documentación referida al modelo final seleccionado, luego de la exploración de poten-ciales candidatos resultantes de aplicar una metodología similar utilizando distintas fuentes de iluminación y tratamiento de los datos.

Análisis exploratorio

Los espectros de la luz dispersada, resultantes de iluminar las muestras con el led con máximo de emisión a 660 nm (fig. 1), y el biplot (fig. 3) no evidencian datos atípicos con lo que se procederá a utilizar todo los datos. Las variables que más varianza en la base de datos generan pueden verse el gráfico de loadings (fig. 2) para cada pixel, en el primer componente principal. Al comparar la fig 2 y la 1 puede verse que las variables que los píxeles que más varianza explican son aquellos que coinciden con los picos del espectro, por lo que se eligió un punto cercano al máximo de emisión (pixel 150). La señal medida por el pixel 431 en función de la turbidez (fig. 4) muestra una tendencia a incrementar con la turbidez linealmente.

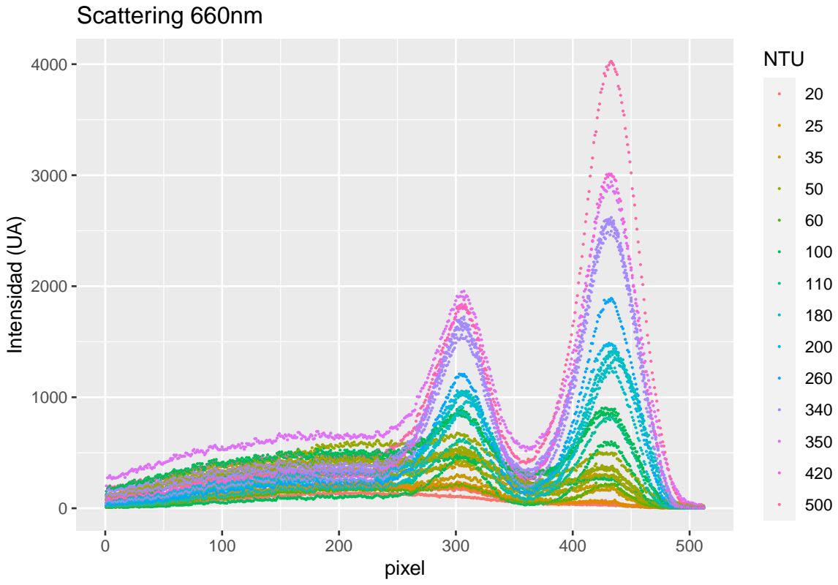
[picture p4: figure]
pixel; Intensidad (UA); NTU; Scattering 660nm

Figure 1: Espectros obtenidos al iluminar la muestra con el LED de 660 nm

Desarrollo del modelo

El modelo con mejor ajuste resultó ser un modelo lineal simple, ajustado con OLS.

NT U = β0 + β1Sp431 + ϵ

Validez El modelo seleccionado no presenta patrones en los observables en el gráfico de residuos vs predichos, corroborando el supuesto de independencia. El supuesto de homocedasticidad se verifica al inspeccionar el gráfico de residuos vs predichos y tras realizar al prueba de Goldfeld-Quandt (pvalgq = 0.2). La tabla ANOVA muestra que el modelo y sus términos son estadísiticamente significativos. La validez del supuesto de normalidad de los residuos no se cumple al rechazar la hipótesis nula de normalidad del test de shapiro wilks (pvalshapirowilks = 0.008) ni mediante la inspección gráfica del QQplot.

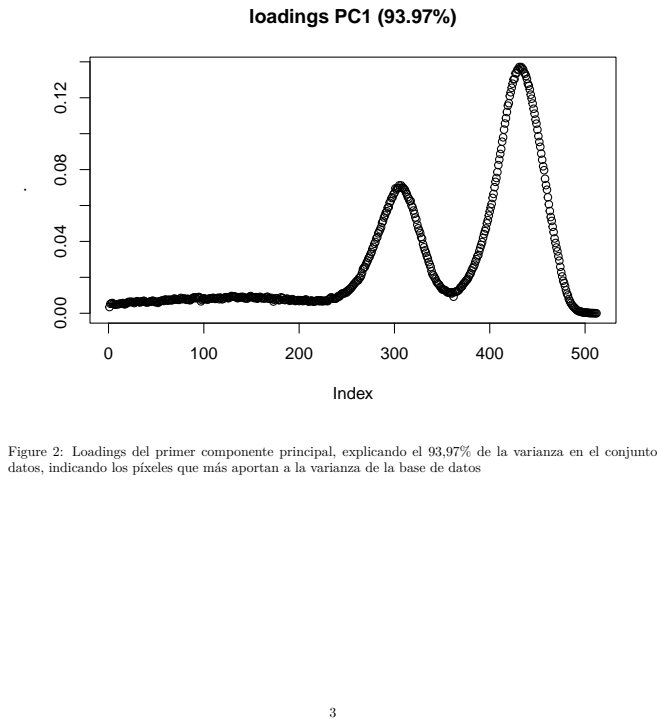
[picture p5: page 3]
loadings PC1 (93.97%); Index

Figure 2: Loadings del primer componente principal, explicando el 93,97% de la varianza en el conjunto
datos, indicando los píxeles que más aportan a la varianza de la base de datos

−0.2 | 0.0 | 0.2 | 0.4

−0.2 0.0 0.2 0.4

# PC1 vs PC2

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
89111012

13
1415

16

17
1819

20

221

23

24

2526

27 28

29 30 31 32

−4000 | 0 2000 | 6000

−4000

0 2000 6000

p170168 p1243927 p15 p52 p203384 p12293 p46251 p501 p31429 p43 p23 p4453835 p454630 p558473 p65 p1p7689523p4 p2106 p173 p215421 p2003196 p2250917 p282261 p1907205 p281319 p290817 p262300 p194201 p192859 p192874 p1808 p104 p231186 p207 p119032 p151672 p193 p12012 p188232 p177238 p156670 p236 p107 p187 p10113 p164 p144611 p237 p121 p175639 p10068 p161235 p9145 p26 p1761453 p13542 p183 p1360918 p125 p182 p110 p1576071 p11562 p15233 p117354 p127432 p240 p124 p152234 p1475881 p1 p1234038 p155439 p13 p166759 p141850 p1224230 p112249 p123244 p576248 p50 p97 p249 p626853 p9860874 p826773 p252 p596172 p4 p251 p847018 p7998375 p69926 p253 p76 p2549189 p4390525 p6257 p89260 p21 p26345 p340 p266 p339 p2678 p338 p269 p270 p337 p271 p336 p272 p335 p2734 p334 p275 p333 p276 p332 p277 p331 p278 p330 p27980 p329 p2812 p328 p283 p327 p284 p326 p285 p325 p286 p324 p2878 p323 p289 p322 p290 p321 p2912 p320 p293 p319 p294 p318 p2956316 p7 p315 p2978314 p299313 p002 p311020 p343 p30869 p3075 p362 p360561 p3975863 p3546567 p3325168 p3094 p3708147 p3726345 p374 p376437 p327841 p3980 p3812 p383 p384 p3856 p3878 p389 p390 p391 p392 p393 p394 p395 p396 p397 p398 p399 p400 p401 p402 p403 p404 p405 p406 p407 p408 p409 p410 p411 p454 p412 p453 p452 p413 p414 p451 p450 p415 p449 p416 p448 p417 p447 p418 p446 p419 p445 p420 p444 p421 p443 p422 p442 p423 p441 p424 p440 p4256 p439 p4387 p428 p436 p429350 p4 4233 p466 p465 p464 p463 p462 p461 p460 p459 p458 p457 p456 p455 p511208 p510607 p594500 p5312498 p976495 p432491 p08948 p7486 p5484 p3 p4821 p480 p479 p478 p477 p476 p475 p474 p473 p472 p471 p470 p469 p468 p467

Figure 3: Biplot de los primeros dos componentes, mostrando ordenamiento de los datos tras la reducción dimensional

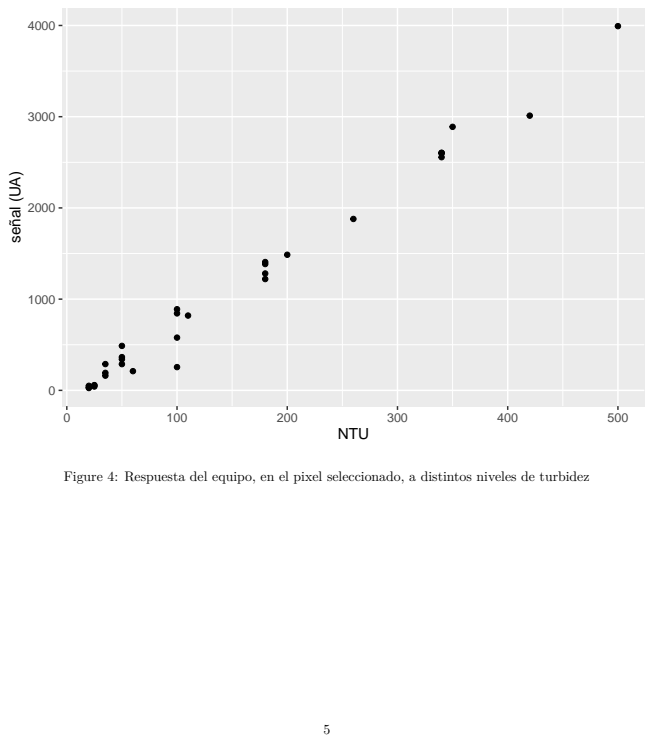
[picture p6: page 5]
NTU; señal (UA)

Figure 4: Respuesta del equipo, en el pixel seleccionado, a distintos niveles de turbidez

## Call:

## lm(formula = .outcome ~ ., data = dat) ##

## Residuals:

## | Min | 1Q | Median | 3Q | Max

## -25.922 | -8.330 | 0.306 | 4.618 | 52.886

## Coefficients:

## | Estimate Std. Error t value Pr(>|t|)

## (Intercept) 15.534626 | 4.022038 | 3.862 0.000557 ***

## p431 | 0.123879 | 0.002604 | 47.564 | < 2e-16 ***

## Signif. codes: 0 ’***’ 0.001 ’**’ 0.01 ’*’ 0.05 ’.’ 0.1 ’ ’ 1 ##

## Residual standard error: 16.11 on 30 degrees of freedom

## Multiple R-squared: | 0.9869, Adjusted R-squared: | 0.9865

## F-statistic: | 2262 on 1 and 30 DF, | p-value: < 2.2e-16

0 | 100 200 300 400 500

−20 40

### Fitted values

### Residuals

## Residuals vs Fitted

X2
X32

X1

−1 1 3

### Standardized residuals

0 100 200 300 400 500

0.0 1.0

### Fitted values

### Stand

### ardize

### d residuals

## Scale−Location

X2
X32 X1

−2 1 3

### Standardized residuals

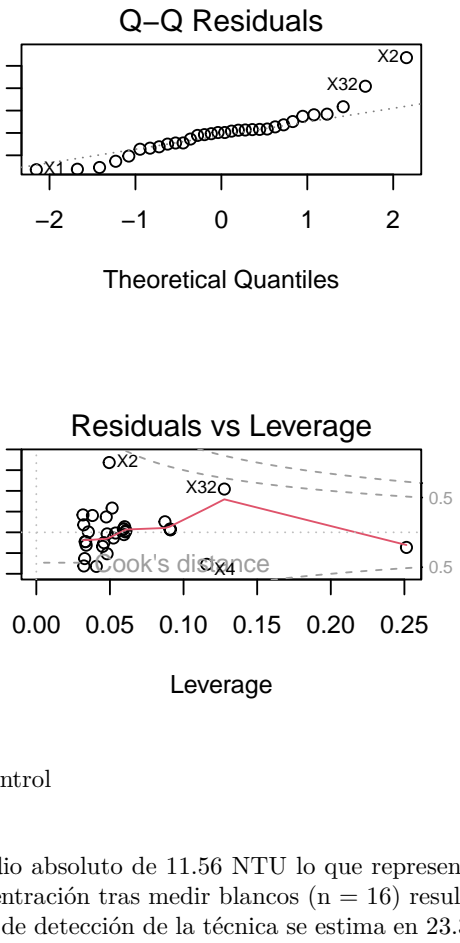
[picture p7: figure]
Theoretical Quantiles; Q−Q Residuals; Leverage; Cook's distance; Residuals vs Leverage

Figure 5: Gráfico de control

Performance El modelo seleccionado presenta un error medio absoluto de 11.56 NTU lo que representa un error medio del 7.8%. El promedio de predicciones de concentración tras medir blancos (n = 16) resultó de 18.36 NTU y el desvío estándar de 1.66, por lo que el límite de detección de la técnica se estima en 23.33 NTU.

RMSE | MAE | Rsquared | errorPorcentualMedio
14.965 | 11.5613 | 0.9897255 | 7.796874

Discusión:

Los resultados muestran que el ecofisiómetro pudo ser calibrado para medir turbidez entre a 23.33 NTU y 500 NTU con un error absoluto promedio de 11.56 NTU, utilizando el siguiente modelo estadístico.

NT Uˆ = 5.54 + 0.12Sp431

Trabajos previos 3 han reportado que los valores de turbidez encontrados en aguas residuales afluentes ronda las 201 ± 114NT U. Esto hace al rango operativo de la curva adecuado a los fines de este estudio, puesto que puede resultaría útil en aproximadamente el 94% de los casos. Al encontrarse el promedio de la curva de calibración (148.28 NTU) cerca de la media ambienta, es esperable que el error porcentual de predicción sea menor. A pesar que se viola el supuesto de normalidad, se considera que los modelos lineales ajustados con OLS son robustos ante falta de normalidad.

Conclusión

Se pudo calibrar un modelo para estimar la turbidez en unidades neftelométricas, acorde a las necesidades del trabajo a realizarse.

Bibliografía

1 - Baird, R.B. et al. (2017) “2130 - turbidity,” in Standard methods for the examination of water and wastewater. 23rd edn. New York: American Public Health Association.

2 - Peris-Díaz, M.D. and Krężel, A. (2021) “A guide to good practice in chemometric methods for vibrational spectroscopy, electrochemistry, and hyphenated Mass Spectrometry,” TrAC Trends in Analytical Chemistry, 135, p. 116157. Available at: https://doi.org/10.1016/j.trac.2020.116157.

3 - Guedes-Alonso, R. et al. (2020) “Pharmaceutical and personal care product residues in a macrophyte pond-constructed wetland treating wastewater from a university campus: Presence, removal and ecological risk assessment,” Science of The Total Environment, 703, p. 135596. Available at: https://doi.org/10.1016/j.scitotenv.2019.135596. (https://doi.org/10.1016/j.scitotenv.2019.135596)

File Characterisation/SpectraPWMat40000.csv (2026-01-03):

0.000000000000000000e+00 | 0.000000000000000000e+00 | 0.000000000000000000e+00 | 0.000000000000000000e+00 | 0.000000000000000000e+00 | 0.000000000000000000e+00 | 0.000000000000000000e+00 | 0.000000000000000000e+00 | 0.000000000000000000e+00 | 0.000000000000000000e+00 | 0.000000000000000000e+00 | 0.000000000000000000e+00 | 0.000000000000000000e+00 | 0.000000000000000000e+00 | 0.000000000000000000e+00 | 0.000000000000000000e+00 | 0.000000000000000000e+00 | 0.000000000000000000e+00 | 0.000000000000000000e+00 | 0.000000000000000000e+00 | 0.000000000000000000e+00 | 0.000000000000000000e+00 | 0.000000000000000000e+00 | 0.000000000000000000e+00 | 0.000000000000000000e+00 | 0.000000000000000000e+00 | 0.000000000000000000e+00 | 0.000000000000000000e+00 | 0.000000000000000000e+00 | 0.000000000000000000e+00 | 0.000000000000000000e+00 | 0.000000000000000000e+00 | 0.000000000000000000e+00 | 0.000000000000000000e+00 | 0.000000000000000000e+00 | 0.000000000000000000e+00 | 0.000000000000000000e+00 | 0.000000000000000000e+00 | 0.000000000000000000e+00 | 0.000000000000000000e+00 | 0.000000000000000000e+00 | 0.000000000000000000e+00 | 0.000000000000000000e+00 | 0.000000000000000000e+00 |
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

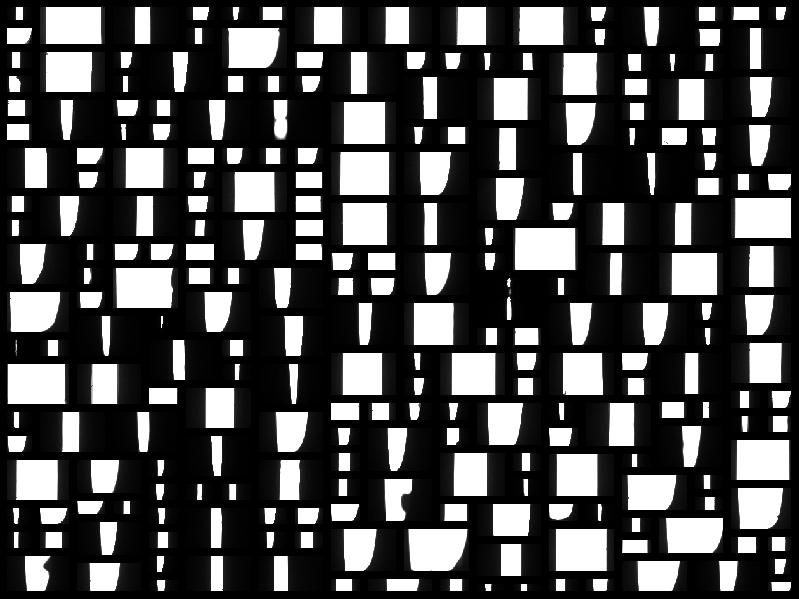
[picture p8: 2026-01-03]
Design/Hardware/Slit/all.jpg

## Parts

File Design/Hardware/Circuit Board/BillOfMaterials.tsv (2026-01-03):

Reference | Value | Datasheet | Footprint | Qty | DNP
C1 | 470 uF 50V | ~ | Capacitor_THT:C_Radial_D10.0mm_H20.0mm_P5.00mm | 1
C2 | 1000 uF 25V | ~ | Capacitor_THT:C_Radial_D8.0mm_H11.5mm_P3.50mm | 1
D1 | 1N5822 | http://www.vishay.com/docs/88526/1n5820.pdf | Diode_THT:D_DO-201AD_P15.24mm_Horizontal | 1
H1,H2,H3 | MountingHole | ~ | MountingHole:MountingHole_5mm | 3
J1,J2 | Conn_01x06_Male | ~ | Connector_Phoenix_MSTB:PhoenixContact_MSTBA_2,5_6-G-5,08_1x06_P5.08mm_Horizontal | 2
J3,J4 | Conn_01x03_Male | ~ | Connector_PinHeader_2.54mm:PinHeader_1x03_P2.54mm_Vertical | 2
J5 | Conn_01x04_Male | ~ | Connector_PinHeader_2.54mm:PinHeader_1x04_P2.54mm_Vertical | 1
J6,J8 | Screw_Terminal_01x02 | ~ | TerminalBlock_Phoenix:TerminalBlock_Phoenix_MKDS-1,5-2_1x02_P5.00mm_Horizontal | 2
J7 | Conn_02x20_Odd_Even | ~ | Connector_PinHeader_2.54mm:PinHeader_2x20_P2.54mm_Vertical | 1
L1 | 33 uH | ~ | Inductor_THT:L_Radial_D7.2mm_P3.00mm_Murata_1700 | 1
Q1,Q2,Q3,Q4,Q5,Q6,Q7,Q8,Q9,Q10 | PN2222A | https://www.onsemi.com/pub/Collateral/PN2222-D.PDF | Package_TO_SOT_THT:TO-92_Inline | 10
R1 | 2.8 | ~ | Resistor_THT:R_Axial_DIN0207_L6.3mm_D2.5mm_P10.16mm_Horizontal | 1
R2 | 5100 | ~ | Resistor_THT:R_Axial_DIN0207_L6.3mm_D2.5mm_P10.16mm_Horizontal | 1
R3,R4,R5,R6,R7,R8,R9,R10,R11 | 560 | ~ | Resistor_THT:R_Axial_DIN0207_L6.3mm_D2.5mm_P10.16mm_Horizontal | 9
R12 | 14 | ~ | Resistor_THT:R_Axial_DIN0207_L6.3mm_D2.5mm_P10.16mm_Horizontal | 1
U1,U3 | LM317_TO-220 | http://www.ti.com/lit/ds/symlink/lm317.pdf | Package_TO_SOT_THT:TO-220-3_Vertical | 2
U2 | LM2596T-5 | http://www.ti.com/lit/ds/symlink/lm2596.pdf | Package_TO_SOT_THT:TO-220-5_P3.4x3.7mm_StaggerOdd_Lead3.8mm_Vertical | 1

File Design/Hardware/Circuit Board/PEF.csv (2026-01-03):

Source: | /home/guido/guido/Proyecto_ecofisiometro/hardware/placa/PEF 2/PEF.kicad_sch
Date: | vie 28 jul 2023 15:07:37
Tool: | Eeschema 6.0.11-2627ca5db0~126~ubuntu20.04.1
Generator: | /usr/share/kicad/plugins/bom_csv_grouped_by_value.py
Component Count: | 40
Individual Components:
Item | Qty | Reference(s) | Value | LibPart | Footprint | Datasheet
 |  | C1 | 470 uF 50V | Device:C | Capacitor_THT:C_Radial_D10.0mm_H20.0mm_P5.00mm | ~
 |  | C2 | 1000 uF 25V | Device:C | Capacitor_THT:C_Radial_D8.0mm_H11.5mm_P3.50mm | ~
 |  | D1 | 1N5822 | Diode:1N5822 | Diode_THT:D_DO-201AD_P15.24mm_Horizontal | http://www.vishay.com/docs/88526/1n5820.pdf
 |  | H1 | MountingHole | Mechanical:MountingHole | MountingHole:MountingHole_5mm | ~
 |  | H2 | MountingHole | Mechanical:MountingHole | MountingHole:MountingHole_5mm | ~
 |  | H3 | MountingHole | Mechanical:MountingHole | MountingHole:MountingHole_5mm | ~
 |  | J1 | Conn_01x06_Male | Connector:Conn_01x06_Male | Connector_Phoenix_MSTB:PhoenixContact_MSTBA_2,5_6-G-5,08_1x06_P5.08mm_Horizontal | ~
 |  | J2 | Conn_01x06_Male | Connector:Conn_01x06_Male | Connector_Phoenix_MSTB:PhoenixContact_MSTBA_2,5_6-G-5,08_1x06_P5.08mm_Horizontal | ~
 |  | J3 | Conn_01x03_Male | Connector:Conn_01x03_Male | Connector_PinHeader_2.54mm:PinHeader_1x03_P2.54mm_Vertical | ~
 |  | J4 | Conn_01x03_Male | Connector:Conn_01x03_Male | Connector_PinHeader_2.54mm:PinHeader_1x03_P2.54mm_Vertical | ~
 |  | J5 | Conn_01x04_Male | Connector:Conn_01x04_Male | Connector_PinHeader_2.54mm:PinHeader_1x04_P2.54mm_Vertical | ~
 |  | J6 | Screw_Terminal_01x02 | Connector:Screw_Terminal_01x02 | TerminalBlock_Phoenix:TerminalBlock_Phoenix_MKDS-1,5-2_1x02_P5.00mm_Horizontal | ~
 |  | J7 | Conn_02x20_Odd_Even | Connector_Generic:Conn_02x20_Odd_Even | Connector_PinHeader_2.54mm:PinHeader_2x20_P2.54mm_Vertical | ~
 |  | J8 | Screw_Terminal_01x02 | Connector:Screw_Terminal_01x02 | TerminalBlock_Phoenix:TerminalBlock_Phoenix_MKDS-1,5-2_1x02_P5.00mm_Horizontal | ~
 |  | L1 | 33 uH | Device:L | Inductor_THT:L_Radial_D7.2mm_P3.00mm_Murata_1700 | ~
 |  | Q1 | PN2222A | Transistor_BJT:PN2222A | Package_TO_SOT_THT:TO-92_Inline | https://www.onsemi.com/pub/Collateral/PN2222-D.PDF
 |  | Q2 | PN2222A | Transistor_BJT:PN2222A | Package_TO_SOT_THT:TO-92_Inline | https://www.onsemi.com/pub/Collateral/PN2222-D.PDF
 |  | Q3 | PN2222A | Transistor_BJT:PN2222A | Package_TO_SOT_THT:TO-92_Inline | https://www.onsemi.com/pub/Collateral/PN2222-D.PDF
 |  | Q4 | PN2222A | Transistor_BJT:PN2222A | Package_TO_SOT_THT:TO-92_Inline | https://www.onsemi.com/pub/Collateral/PN2222-D.PDF
 |  | Q5 | PN2222A | Transistor_BJT:PN2222A | Package_TO_SOT_THT:TO-92_Inline | https://www.onsemi.com/pub/Collateral/PN2222-D.PDF
 |  | Q6 | PN2222A | Transistor_BJT:PN2222A | Package_TO_SOT_THT:TO-92_Inline | https://www.onsemi.com/pub/Collateral/PN2222-D.PDF
 |  | Q7 | PN2222A | Transistor_BJT:PN2222A | Package_TO_SOT_THT:TO-92_Inline | https://www.onsemi.com/pub/Collateral/PN2222-D.PDF
 |  | Q8 | PN2222A | Transistor_BJT:PN2222A | Package_TO_SOT_THT:TO-92_Inline | https://www.onsemi.com/pub/Collateral/PN2222-D.PDF
 |  | Q9 | PN2222A | Transistor_BJT:PN2222A | Package_TO_SOT_THT:TO-92_Inline | https://www.onsemi.com/pub/Collateral/PN2222-D.PDF
 |  | Q10 | PN2222A | Transistor_BJT:PN2222A | Package_TO_SOT_THT:TO-92_Inline | https://www.onsemi.com/pub/Collateral/PN2222-D.PDF
 |  | R1 | 2.8 | Device:R | Resistor_THT:R_Axial_DIN0207_L6.3mm_D2.5mm_P10.16mm_Horizontal | ~
 |  | R2 | 5100 | Device:R | Resistor_THT:R_Axial_DIN0207_L6.3mm_D2.5mm_P10.16mm_Horizontal | ~
 |  | R3 | 560 | Device:R | Resistor_THT:R_Axial_DIN0207_L6.3mm_D2.5mm_P10.16mm_Horizontal | ~
 |  | R4 | 560 | Device:R | Resistor_THT:R_Axial_DIN0207_L6.3mm_D2.5mm_P10.16mm_Horizontal | ~
 |  | R5 | 560 | Device:R | Resistor_THT:R_Axial_DIN0207_L6.3mm_D2.5mm_P10.16mm_Horizontal | ~
 |  | R6 | 560 | Device:R | Resistor_THT:R_Axial_DIN0207_L6.3mm_D2.5mm_P10.16mm_Horizontal | ~
 |  | R7 | 560 | Device:R | Resistor_THT:R_Axial_DIN0207_L6.3mm_D2.5mm_P10.16mm_Horizontal | ~
 |  | R8 | 560 | Device:R | Resistor_THT:R_Axial_DIN0207_L6.3mm_D2.5mm_P10.16mm_Horizontal | ~
 |  | R9 | 560 | Device:R | Resistor_THT:R_Axial_DIN0207_L6.3mm_D2.5mm_P10.16mm_Horizontal | ~
 |  | R10 | 560 | Device:R | Resistor_THT:R_Axial_DIN0207_L6.3mm_D2.5mm_P10.16mm_Horizontal | ~
 |  | R11 | 560 | Device:R | Resistor_THT:R_Axial_DIN0207_L6.3mm_D2.5mm_P10.16mm_Horizontal | ~
 |  | R12 | 14 | Device:R | Resistor_THT:R_Axial_DIN0207_L6.3mm_D2.5mm_P10.16mm_Horizontal | ~
 |  | U1 | LM317_TO-220 | Regulator_Linear:LM317_TO-220 | Package_TO_SOT_THT:TO-220-3_Vertical | http://www.ti.com/lit/ds/symlink/lm317.pdf
 |  | U2 | LM2596T-5 | Regulator_Switching:LM2596T-5 | Package_TO_SOT_THT:TO-220-5_P3.4x3.7mm_StaggerOdd_Lead3.8mm_Vertical | http://www.ti.com/lit/ds/symlink/lm2596.pdf
 |  | U3 | LM317_TO-220 | Regulator_Linear:LM317_TO-220 | Package_TO_SOT_THT:TO-220-3_Vertical | http://www.ti.com/lit/ds/symlink/lm317.pdf
Collated Components:
Item | Qty | Reference(s) | Value | LibPart | Footprint | Datasheet
1 | 1 | C1 | 470 uF 50V | Device:C | Capacitor_THT:C_Radial_D10.0mm_H20.0mm_P5.00mm | ~
2 | 1 | C2 | 1000 uF 25V | Device:C | Capacitor_THT:C_Radial_D8.0mm_H11.5mm_P3.50mm | ~
3 | 1 | D1 | 1N5822 | Diode:1N5822 | Diode_THT:D_DO-201AD_P15.24mm_Horizontal | http://www.vishay.com/docs/88526/1n5820.pdf
4 | 3 | H1, H2, H3 | MountingHole | Mechanical:MountingHole | MountingHole:MountingHole_5mm | ~
5 | 2 | J1, J2 | Conn_01x06_Male | Connector:Conn_01x06_Male | Connector_Phoenix_MSTB:PhoenixContact_MSTBA_2,5_6-G-5,08_1x06_P5.08mm_Horizontal | ~
6 | 2 | J3, J4 | Conn_01x03_Male | Connector:Conn_01x03_Male | Connector_PinHeader_2.54mm:PinHeader_1x03_P2.54mm_Vertical | ~
7 | 1 | J5 | Conn_01x04_Male | Connector:Conn_01x04_Male | Connector_PinHeader_2.54mm:PinHeader_1x04_P2.54mm_Vertical | ~
8 | 2 | J6, J8 | Screw_Terminal_01x02 | Connector:Screw_Terminal_01x02 | TerminalBlock_Phoenix:TerminalBlock_Phoenix_MKDS-1,5-2_1x02_P5.00mm_Horizontal | ~
9 | 1 | J7 | Conn_02x20_Odd_Even | Connector_Generic:Conn_02x20_Odd_Even | Connector_PinHeader_2.54mm:PinHeader_2x20_P2.54mm_Vertical | ~
10 | 1 | L1 | 33 uH | Device:L | Inductor_THT:L_Radial_D7.2mm_P3.00mm_Murata_1700 | ~
11 | 10 | Q1, Q2, Q3, Q4, Q5, Q6, Q7, Q8, Q9, Q10 | PN2222A | Transistor_BJT:PN2222A | Package_TO_SOT_THT:TO-92_Inline | https://www.onsemi.com/pub/Collateral/PN2222-D.PDF
12 | 1 | R1 | 2.8 | Device:R | Resistor_THT:R_Axial_DIN0207_L6.3mm_D2.5mm_P10.16mm_Horizontal | ~
13 | 1 | R2 | 5100 | Device:R | Resistor_THT:R_Axial_DIN0207_L6.3mm_D2.5mm_P10.16mm_Horizontal | ~
14 | 9 | R3, R4, R5, R6, R7, R8, R9, R10, R11 | 560 | Device:R | Resistor_THT:R_Axial_DIN0207_L6.3mm_D2.5mm_P10.16mm_Horizontal | ~
15 | 1 | R12 | 14 | Device:R | Resistor_THT:R_Axial_DIN0207_L6.3mm_D2.5mm_P10.16mm_Horizontal | ~
16 | 2 | U1, U3 | LM317_TO-220 | Regulator_Linear:LM317_TO-220 | Package_TO_SOT_THT:TO-220-3_Vertical | http://www.ti.com/lit/ds/symlink/lm317.pdf
17 | 1 | U2 | LM2596T-5 | Regulator_Switching:LM2596T-5 | Package_TO_SOT_THT:TO-220-5_P3.4x3.7mm_StaggerOdd_Lead3.8mm_Vertical | http://www.ti.com/lit/ds/symlink/lm2596.pdf

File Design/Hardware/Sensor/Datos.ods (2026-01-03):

Part | SP1 | SP2 | SP3 | SP4 | SP5 | Size (mm) | Shape | External References |  |  |  | Design specification |  | unit
Sensor case | Sensor Holder | Outer |  |  | Height | 23.9 |  | Part | Subpart | Parameter |  | Max wavelength | 800 | nm
 |  |  |  |  | Base | 29 |  | Camera | PCB | Height | 23.7 | Min wavelength | 350 | nm
 |  |  |  |  | Thickness | 5.1 |  |  |  | Base | 24.8 | Max colimated light angle | 0.1 | deg
 |  |  |  |  | Angle | 36.8087087344393 |  |  |  | Thickness | 0.9 | wall Thickness | 2 | mm
 |  |  |  |  | Distance to origin | 6.09918880837985 |  |  | Sensor casing | Base | 8.44 | tolerance | 0.2 | mm
 |  | inner |  |  | Height | 23.9 |  |  |  | Height | 8.4 | min angle | 20.4873151147227 | deg | 0.35757110364551
 |  |  |  |  | Base | 25 |  |  |  | Thickness | 3 | max angle | 53.130102354156 | deg | 0.927295218001612
 |  |  |  |  | Thickness | 1.1 |  |  |  | Vertical center rel to socket | 13.42 | delta min max | 32.6427872394333 | deg | 0.569724114356102
 | Slit Holder |  |  |  | wall thickness | 5.2 |  |  |  | Vertical center rel to bottom | 10.28 | fraction of margin sensor as buffer | 0.05
 |  |  |  |  | Base | 20.2 |  |  | Sensor | Height | 2.74 | fraction of sensor used | 0.95
 |  |  |  |  | Height | 23.9 |  |  |  | Base | 3.76
 |  |  |  |  | slit aperture | 10.2 |  | Slit | Structure | Height | 23.7
 |  |  |  |  | Distance between slits | 34.3774328012573 |  |  |  | Base | 10
 | Connector to cell | lateral socket |  |  |  |  |  |  |  | Thickness | 1
 |  |  |  |  |  |  |  |  |  | Vertical Apterure | 2.74
 |  |  |  |  |  |  |  |  |  | Horizontal aperture | 0.06
 |  |  |  |  |  |  |  | Diffraction Gratting |  | lines per mm | 1000
 |  |  |  |  |  |  |  | Front Cap | Sample input | Height | 26
 |  |  |  |  |  |  |  |  |  | Base | 26
 |  |  |  |  |  |  |  |  |  | Thickness | 9.12
 |  |  |  |  |  |  |  |  |  | Distance to center | 5

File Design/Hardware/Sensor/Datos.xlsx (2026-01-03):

Part | SP1 | SP2 | SP3 | SP4 | SP5 | Size (mm) | Shape | External References |  |  |  | Design specification |  | unit
Sensor case | Sensor Holder | Outer |  |  | Height | 46 |  | Part | Subpart | Parameter |  | Max wavelength | 800 | nm
 |  |  |  |  | Base | 29 |  | Camera | PCB | Height | 23.7 | Min wavelength | 350 | nm
 |  |  |  |  | Thickness | 5.1 |  |  |  | Base | 24.8 | Max colimated light angle | 0.1 | deg
 |  |  |  |  | Angle | 36.80870873 |  |  |  | Thickness | 0.9 | wall Thickness | 2 | mm
 |  |  |  |  | Distance to origin | 6.099188808 |  |  | Sensor casing | Base | 8.44 | tolerance | 0.2 | mm
 |  | inner |  |  | Height | 36.42 |  |  |  | Height | 8.4 | min angle | 20.48731511 | deg | 0.3575711036
 |  |  |  |  | Base | 25 |  |  |  | Thickness | 3 | max angle | 53.13010235 | deg | 0.927295218
 |  |  |  |  | Thickness | 1.1 |  |  |  | Vertical center rel to bottom | 13.42 | delta min max | 32.64278724 | deg | 0.5697241144
 |  |  |  |  | side | 1 |  |  |  | Vertical center rel to top (socket) | 10.28 | fraction of margin sensor as buffer | 0.05
 | Slit Holder |  |  |  | wall thickness | 5.2 |  |  |  | side margin | 1.2 | fraction of sensor used | 0.95
 |  |  |  |  | Base | 20.2 |  |  | Sensor | Height | 2.74 | N battery | 4
 |  |  |  |  | Height | 46 |  |  |  | Base | 3.76 | Battery per side | 2
 |  |  |  |  | slit aperture | 10.2 |  | Slit | Structure | Height | 23.7
 |  |  |  |  | Distance between slits | 34.3774328 |  |  |  | Base | 10
 | Connector to cell | lateral socket |  |  | Height | 26.2 |  |  |  | Thickness | 1
 |  |  |  |  | Base | 24.8 |  |  |  | Vertical Apterure | 2.74
 |  |  |  |  | Depth | 10 |  |  |  | Horizontal aperture | 0.06
 |  |  |  |  | Distance from center | 5 |  | Diffraction Gratting |  | lines per mm | 1000
 |  |  | opening for tube |  | Height | 1.5 |  | Front Cap | Socket imput | Height | 26
 |  |  |  |  | Base | 8.55 | (from edge to edge) |  |  | Base | 24.6
 |  |  |  |  | Depth | 10 |  |  |  | Thickness | 9.8
 |  | optical window |  |  | Diameter | 5 |  |  |  | Distance to center | 4
 |  |  |  |  | Depth | 5 |  | Battery |  | Height | 23
 |  |  |  |  |  |  |  |  |  | Base | 23
 |  |  |  |  |  |  |  |  |  | Thickness | 80

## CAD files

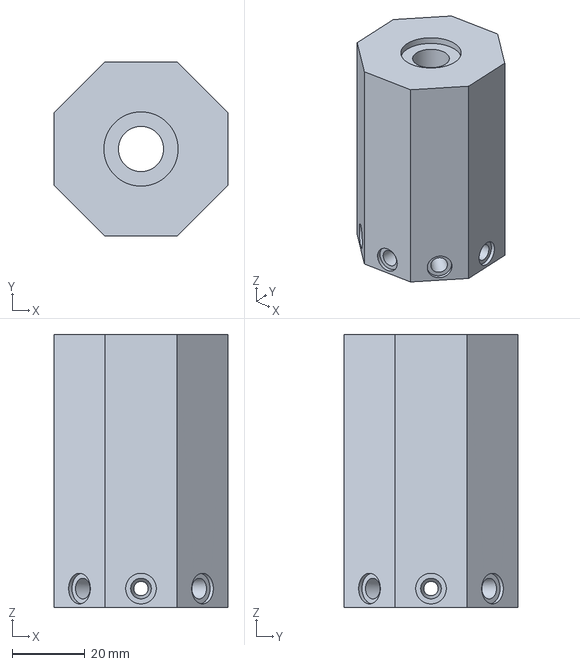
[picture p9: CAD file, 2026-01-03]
Design/Hardware/Cell/LED Holder-XL-LED holder.3mf
47.8 x 47.8 x 75.0 mm

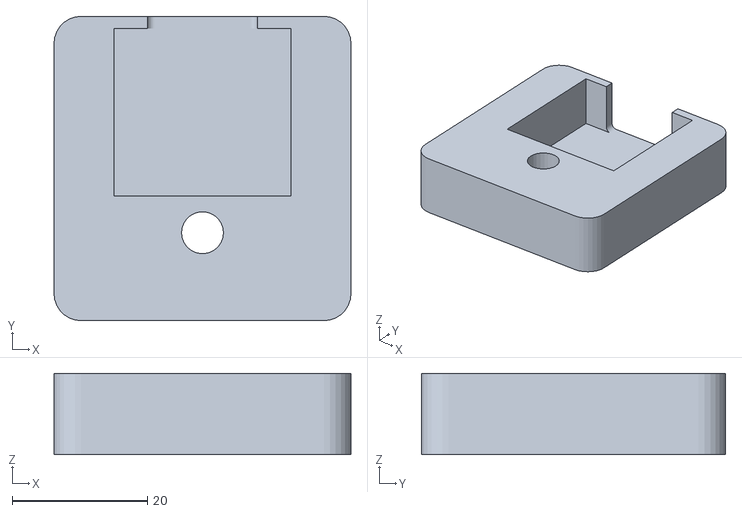
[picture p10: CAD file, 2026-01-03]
Design/Hardware/LED Holder/LED Holder.stl
43.9 x 45.0 x 12.0

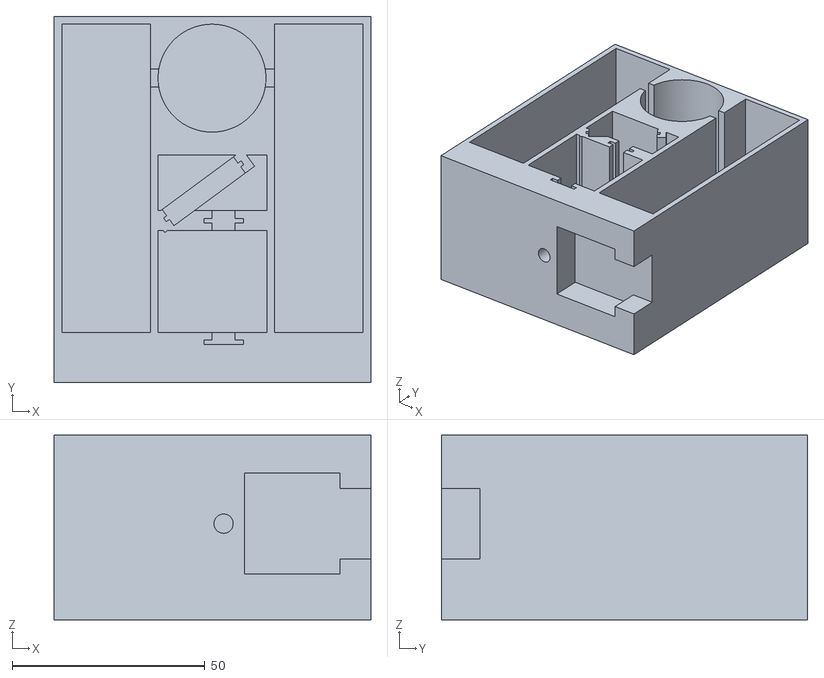
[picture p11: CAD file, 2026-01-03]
Design/Hardware/Sensor/prueba.stl
82.2 x 95.0 x 48.0

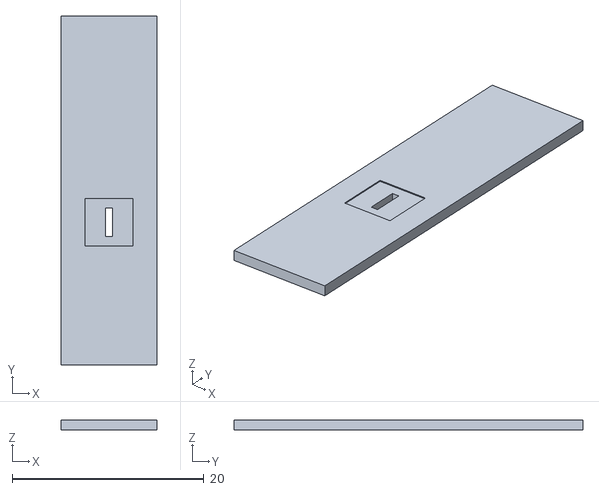
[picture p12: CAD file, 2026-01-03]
Design/Hardware/Slit/Slit 0.7.stl
10.0 x 36.4 x 1.00

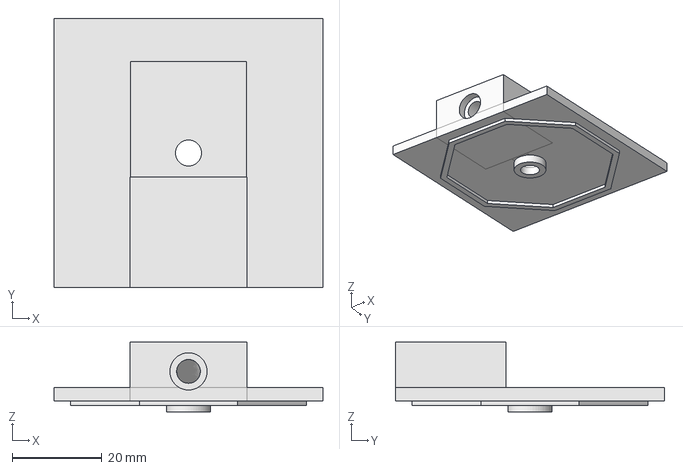
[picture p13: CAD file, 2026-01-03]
Design/Hardware/Cell/Frontal Cap5.FCStd
60.0 x 60.0 x 15.6 mm

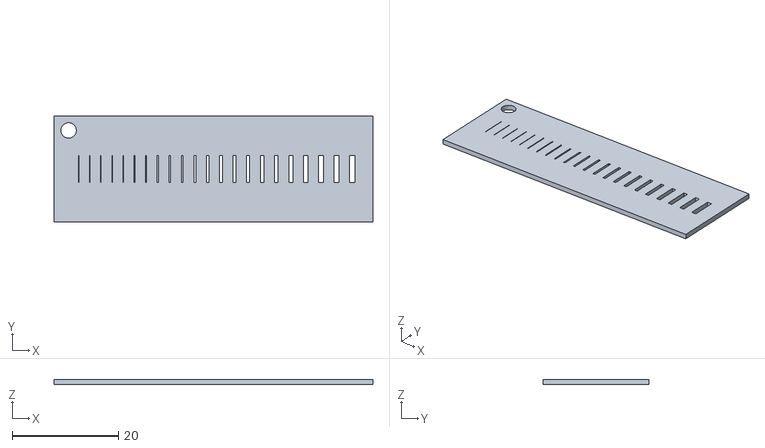
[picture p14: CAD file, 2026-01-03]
Design/Hardware/Slit/CALIBRATION TEST-Body.stl
60.0 x 20.0 x 1.00

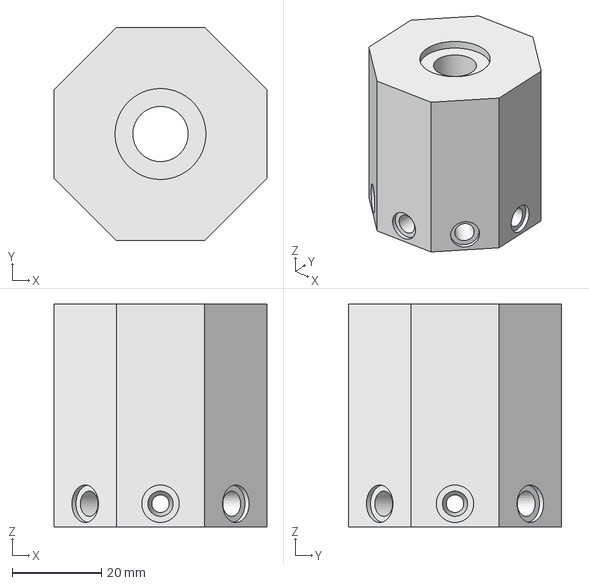
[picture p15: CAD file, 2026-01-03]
Design/Hardware/Cell/LED Holder-L.FCStd
47.8 x 47.8 x 50.0 mm

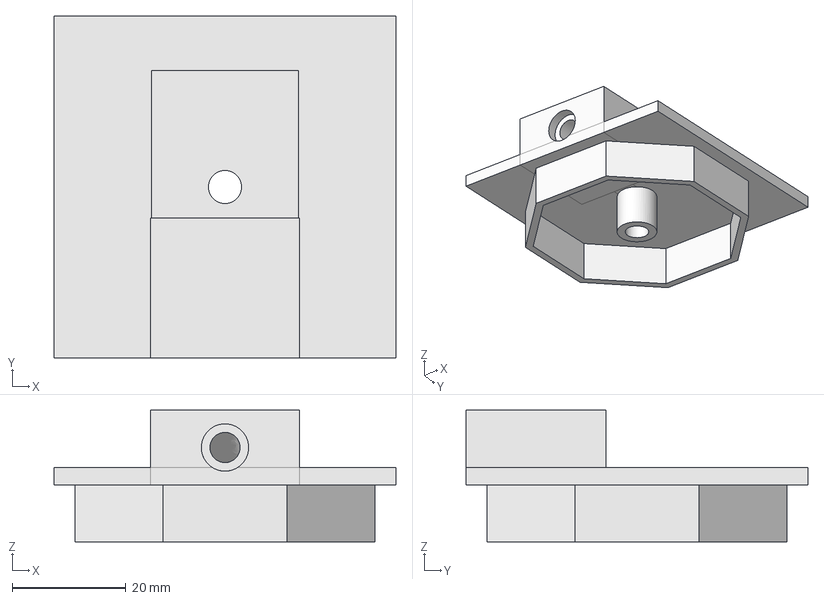
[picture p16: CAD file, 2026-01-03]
Design/Hardware/Cell/back Cap5.FCStd
60.0 x 60.0 x 23.1 mm

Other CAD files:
Design/Hardware/LED Holder/LED holder 1.FCStd
Design/Hardware/Sensor/Sensor 1.FCStd
Design/Hardware/Slit/Slit 0.2.stl
Design/Hardware/Cell/LED Holder-XL.FCStd
Design/Hardware/Sensor/Sensor 1-Body.stl
Design/Hardware/Cell/Frontal Cap5-Frontal Cap.3mf
Design/Hardware/Slit/Slit.FCStd
Design/Hardware/Slit/Slit 0.8.stl
Design/Hardware/Slit/Slit 0.5.stl
Design/Hardware/Cell/LED Holder-L-LED holder.3mf
Design/Hardware/Cell/LED Holder-LED holder.3mf
Design/Hardware/Cell/LED Holder.FCStd
Design/Hardware/Cell/back Cap5.3mf
Design/Hardware/Slit/CALIBRATION TEST.FCStd
Design/Hardware/Slit/Slit 0.3.stl
Design/Hardware/Slit/Slit 0.4.stl
Design/Hardware/Slit/Slit 0.6.stl
Design/Hardware/Slit/Slit gruesa.stl
Design/Hardware/Slit/Slit test.FCStd
Design/Hardware/Slit/Slit wide-Body.stl
Design/Hardware/Slit/Slit wide.FCStd
Design/Hardware/Slit/Slit.stl
Design/Hardware/Slit/prueba.stl

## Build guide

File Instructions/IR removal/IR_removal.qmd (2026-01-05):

---
title: "Tutorial: Removing the IR Filter from a Raspberry Pi Camera V1.3"
format: pdf
editor: visual
---

This guide details the process of modifying a standard Raspberry Pi Camera (V1.3) by removing its internal Infrared (IR) cut-off filter. This modification is essential for the Ecophysiometer, allowing the sensor to detect the near-IR wavelengths needed for comprehensive absorbance and fluorescence measurements.

## IMPORTANT DISCLAIMER

This is a high-risk, delicate procedure. By proceeding, you accept the risk that you may permanently destroy your Raspberry Pi Camera. The actual image sensor is extremely fragile; touching it, scratching it, or getting debris on it will render the camera useless.

Though the process is straight forward for V2 cameras and there's even a no-IR filter alternative, this is not the case for V1.3 cameras. Thus, the intent of this tutorial is to describe the necessary steps to remove the lens and the IR filter of the camera so it serves its role as the sensor.

Basically, the goal is to go through the steps necessary to do this transition:

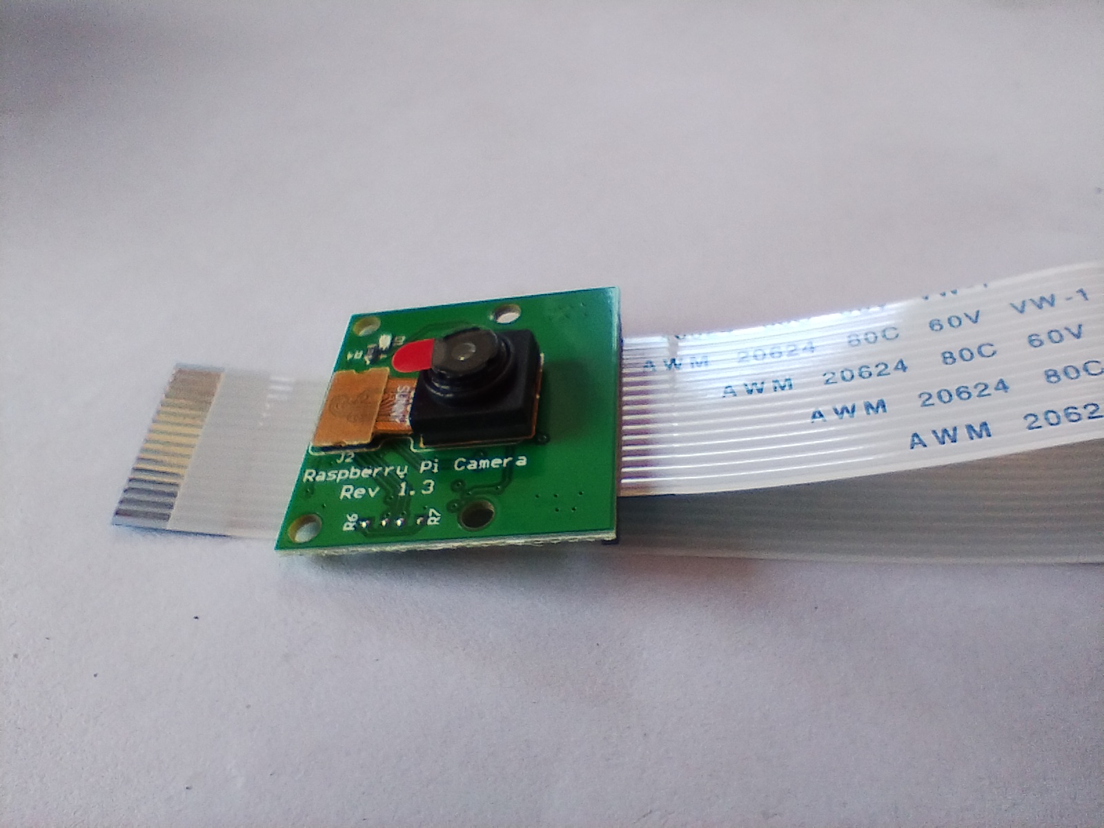
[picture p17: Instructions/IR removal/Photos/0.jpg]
Standard Raspberry Pi Camera Module V1.3 with ribbon cable before modification.
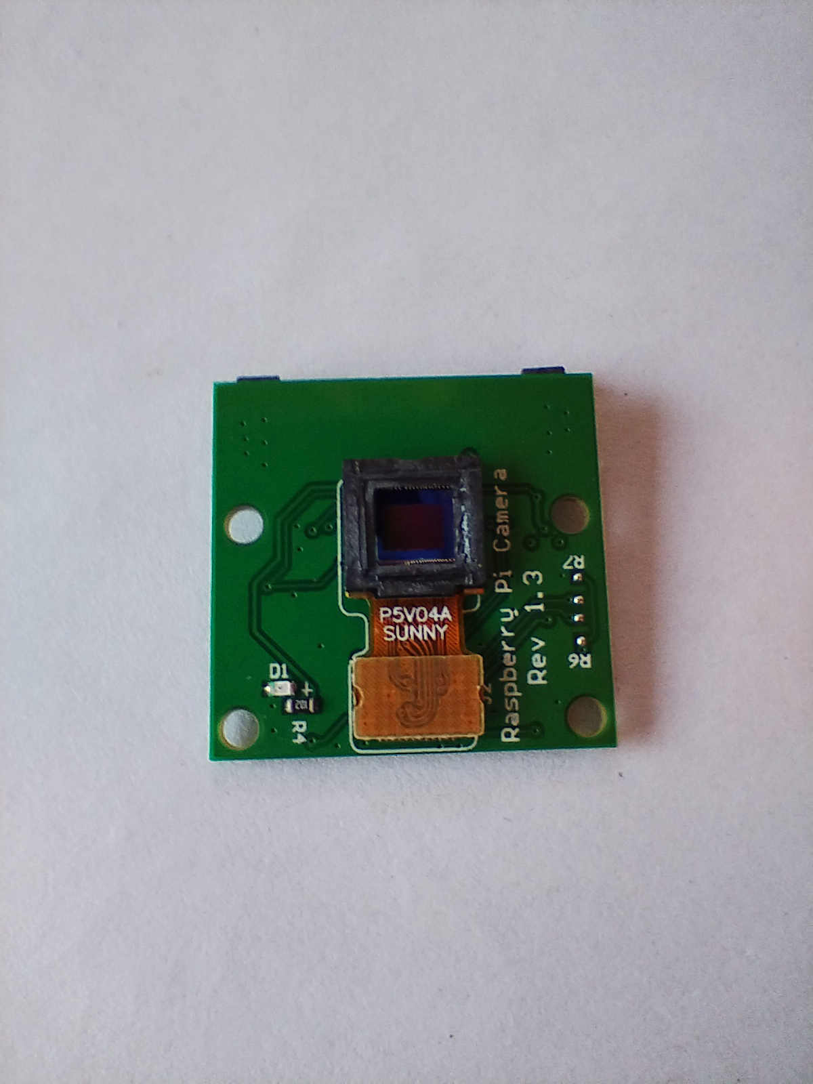
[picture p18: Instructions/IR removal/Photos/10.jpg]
final sensor
 <font size=35>⮕ </font> 

Before handling the camera, you must protect the electronic components from Electrostatic Discharge (ESD). A tiny spark you cannot even feel can permanently "brick" the camera sensor.

-   Best Practice: Wear an anti-static wrist strap connected to a known ground.

-   Alternative: If you do not have professional ESD gear, work barefoot while maintaining contact with a non-insulated floor (like stone or tile) to dissipate static buildup.

-   Workspace: Avoid working on carpets or wearing wool/synthetic clothing that generates static.

-   Secure the Board: Use a small amount of adhesive putty to fix the camera board to your clean workspace to prevent it from slipping during the delicate prying steps.

## Tools Required

-   1x Raspberry Pi Camera V1.3

-   1x Precision hobby knife or scalpel (e.g., X-Acto knife with a fine, sharp blade)

-   1x Fine-tip tweezers

-   Adhesive putty (e.g., Blu-Tack) or double-sided tape (to secure the camera board)

-   A well-lit, clean workspace (a magnification lamp is highly recommended)

-   Optional but recommended: Small, clean, soft-bristled brush (like a camera lens brush) or a can of compressed air.

## Understanding the Components

Before you start, familiarize yourself with the anatomy of the camera module. These are not formal names, but helpfully will help us avoid confusion:

-   **Camera Board**: The green printed circuit board. This is the part that communicates the raspberry pi with the sensor, making it a functional camera.

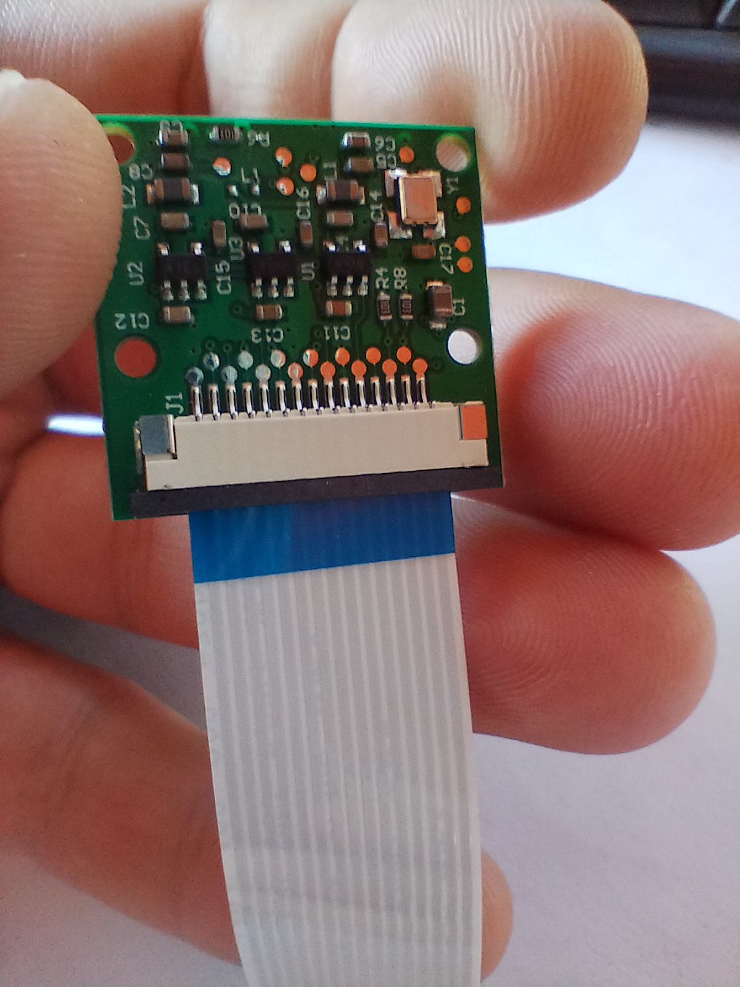
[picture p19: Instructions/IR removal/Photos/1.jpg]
Standard Raspberry Pi Camera Module V1.3 board.


-   **Black Plastic Holder**: The square plastic glued to the board. It comes with double tape which you have to peel of so yuo can glue it to the board for it to stay at a fixed position. It contains the lens, the IR filter and the sensor.

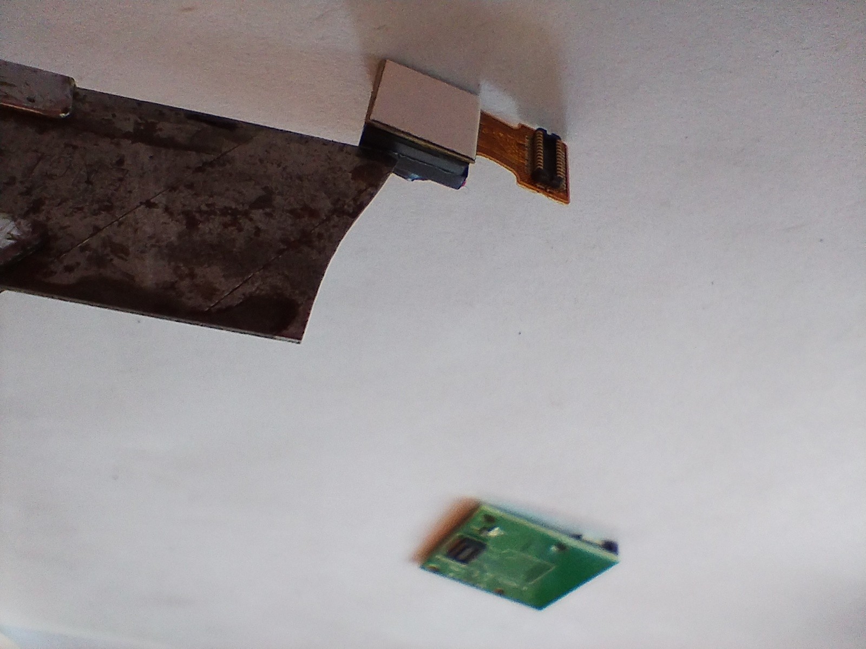
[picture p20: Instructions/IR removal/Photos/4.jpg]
Plastic holder, containing the sensor and the optical components


-   **Lens Assembly**: The circular, threaded part screwed into the holder.

-   **IR Filter**: A tiny, square piece of glass (often with a greenish or yellowish coating) located inside the black plastic holder, directly above the actual sensor chip. This is your target.

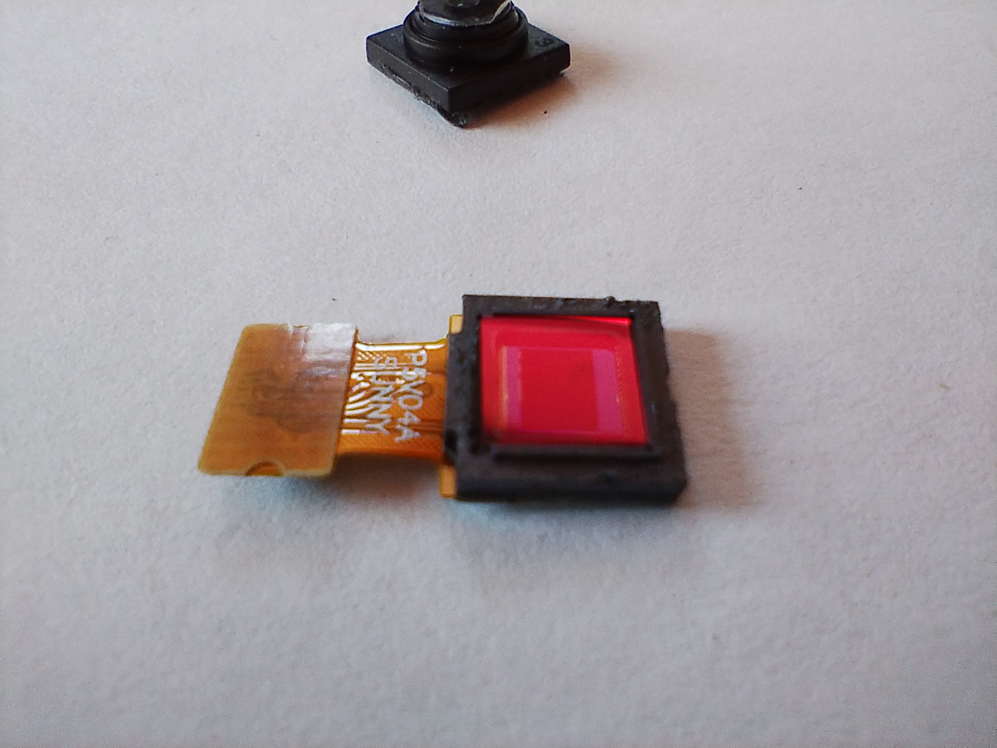
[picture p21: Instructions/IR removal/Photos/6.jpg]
View of the optical component with the lens removed, exposing the IR filter (redish colour)


## Step-by-Step Guide

### Step 1: Preparation

Secure the Raspberry Pi Camera board to your workspace using a small amount of adhesive putty or double-sided tape. This prevents the board from slipping while you perform the delicate cuts. Ensure your workspace is as dust-free as possible.

### Step 2: Unplug the Black Plastic Holder so you can comfortably work on it.

### Step 3: Cutting away the Plastic Holder

This is the most critical and dangerous step. Your goal is to separate the black plastic holder from the red circuit board without the knife slipping and destroying the sensor chip underneath.

Use the tip of your scalpel to apply gentle, persistent pressure at one of the corners where the plastic holder meets the red board. The holder is held on by a strong adhesive.

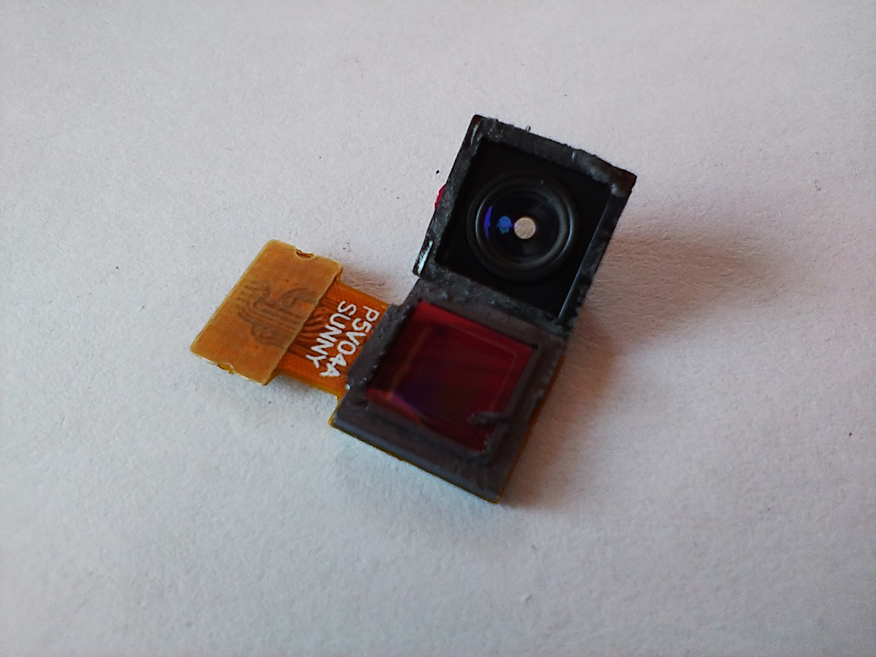
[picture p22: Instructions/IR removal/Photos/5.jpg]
Applying gentle, persistent pressure with a precision blade at the corner of the black plastic holder.


Continue carefully prying at each corner. Do not rush. You are trying to break the glue's bond, not cut through the board itself.

As the glue starts to give, the holder will lift. Carefully remove it. Do not touch the silver sensor chip exposed on the board.

### Step 4: Removing the IR Filter

Now that the holder is removed, look inside it from the bottom (the side that was glued to the board). You will see the tiny, square IR cut-off filter.

Camera with the square IR filter exposed

The filter is typically held in place by a ring of adhesive. Use the very tip of your scalpel to carefully pry the edge of the glass filter.

Apply gentle pressure until the filter pops out of the plastic holder. You can now dispose of the filter.

Verification: Ensure no broken glass shards or debris are left inside the plastic holder. Use a clean, soft brush or compressed air to remove any contaminants. Do not blow on it with your mouth.

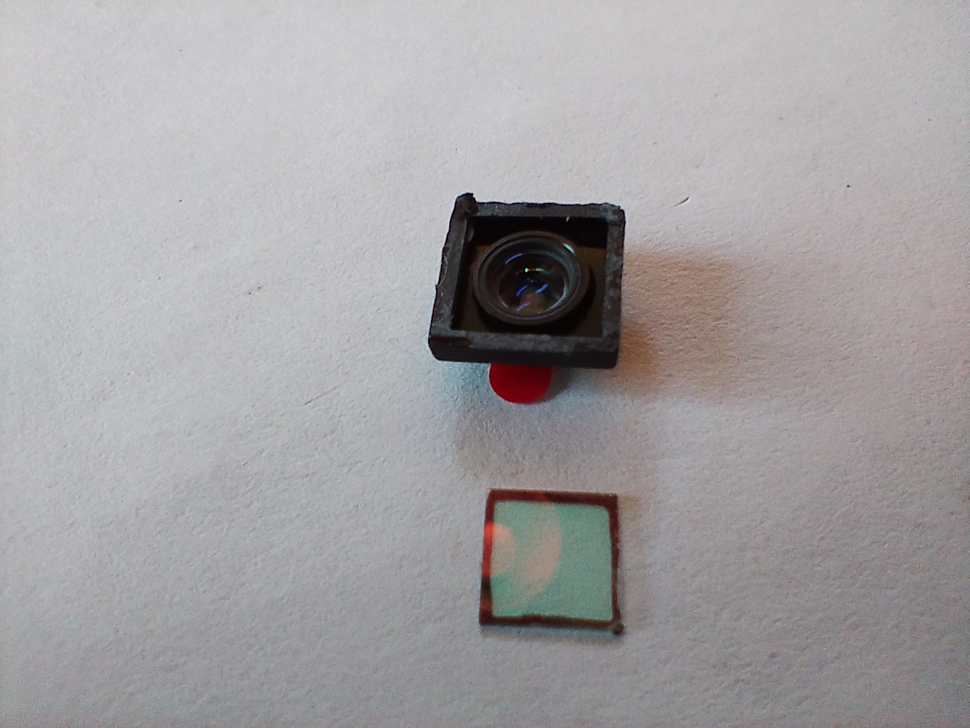
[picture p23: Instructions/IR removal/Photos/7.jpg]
The successfully removed square glass IR filter alongside the lens assembly.


### Step 5: Reassembly

Look closely at the silver sensor chip on the red board. It must be perfectly clean. If there is any debris, very carefully remove it with a clean brush or compressed air. NEVER touch the sensor surface with your fingers, a cloth, or any hard tool.

Mount the sensor back into the board by plugging the connector. Peel of the tape to fix the sensor to the board. At the end, the camera should look like this:

End result: Sensor was fixed with the tape and ribbon was plugged into the board's connector during reassembly 

When gluing the plastic holder back onto the board, ensure it is perfectly centered over the sensor chip to prevent horizontal spectral offsets in the ImageProcessor.py alignment phase.

## Testing Your Modified Camera

Put it inside the Ecophysiometer housing and try taking a photo with the white absorbance LED turned on. You whould be able to see a rainbow:

Representative rainbow spectrum captured by the modified sensor inside the housing to verify successful IR filter removal.

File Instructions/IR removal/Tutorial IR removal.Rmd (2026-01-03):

---
title: "IR filter removal tutorial"
author: "Guido Marconi"
date: "`r Sys.Date()`"
output: html_document
---

```{r setup, include=FALSE}
knitr::opts_chunk$set(echo = TRUE)
print(getwd())
```

# How to remove IR filter from V1.3 raspberry pi cameras?

Though the process is straight foward for V2 cameras and there's even a no-IR filter alternative, this is not the case for V1.3 cameras. Thus, the intent of this tutorial is to describe the necesary steps to remove the lens and the IR filter of the camera so it serves its role as the sensor.

Basically, the goal is to go through the steps necessary to do this transition: 

original camera <font size=15>⮕  </font> final sensor

The first caution you need to have is that of static discharges. If you have static wrist band or another caution device, use them. Any discharge can damage or permanently break your camera. If you don't have that kind of element you can also be bearfooted touching the ground wile working.

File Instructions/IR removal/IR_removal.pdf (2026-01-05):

# Tutorial: Removing the IR Filter from a Raspberry Pi Camera V1.3

This guide details the process of modifying a standard Raspberry Pi Camera (V1.3) by removing its internal Infrared (IR) cut-off filter. This modification is essential for the Ecophysiometer, allowing the sensor to detect the near-IR wavelengths needed for comprehensive absorbance and fluorescence measurements.

IMPORTANT DISCLAIMER

This is a high-risk, delicate procedure. By proceeding, you accept the risk that you may permanently destroy your Raspberry Pi Camera. The actual image sensor is extremely fragile; touching it, scratching it, or getting debris on it will render the camera useless.

Though the process is straight forward for V2 cameras and there’s even a no-IR filter alternative, this is not the case for V1.3 cameras. Thus, the intent of this tutorial is to describe the necessary steps to remove the lens and the IR filter of the camera so it serves its role as the sensor.

Basically, the goal is to go through the steps necessary to do this transition:

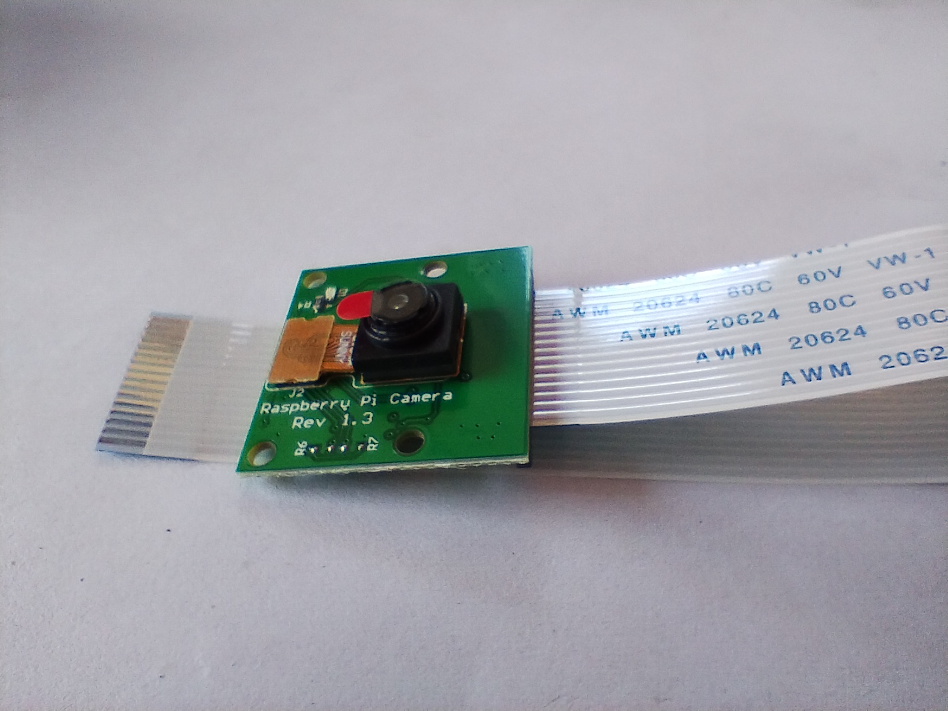
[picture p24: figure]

Before handling the camera, you must protect the electronic components from Electrostatic Discharge (ESD). A tiny spark you cannot even feel can permanently “brick” the camera sensor.

1

- Best Practice: Wear an anti-static wrist strap connected to a known ground.
- Alternative: If you do not have professional ESD gear, work barefoot while maintaining contact with a non-insulated floor (like stone or tile) to dissipate static buildup.
- Workspace: Avoid working on carpets or wearing wool/synthetic clothing that generates static.
- Secure the Board: Use a small amount of adhesive putty to fix the camera board to your clean workspace to prevent it from slipping during the delicate prying steps.

Tools Required

- 1x Raspberry Pi Camera V1.3
- 1x Precision hobby knife or scalpel (e.g., X-Acto knife with a fine, sharp blade)
- 1x Fine-tip tweezers
- Adhesive putty (e.g., Blu-Tack) or double-sided tape (to secure the camera board)
- A well-lit, clean workspace (a magnification lamp is highly recommended)
- Optional but recommended: Small, clean, soft-bristled brush (like a camera lens brush) or a can of compressed air.

Understanding the Components

Before you start, familiarize yourself with the anatomy of the camera module. These are not formal names, but helpfully will help us avoid confusion:

- Camera Board: The green printed circuit board. This is the part that communicates the raspberry pi with the sensor, making it a functional camera.

2

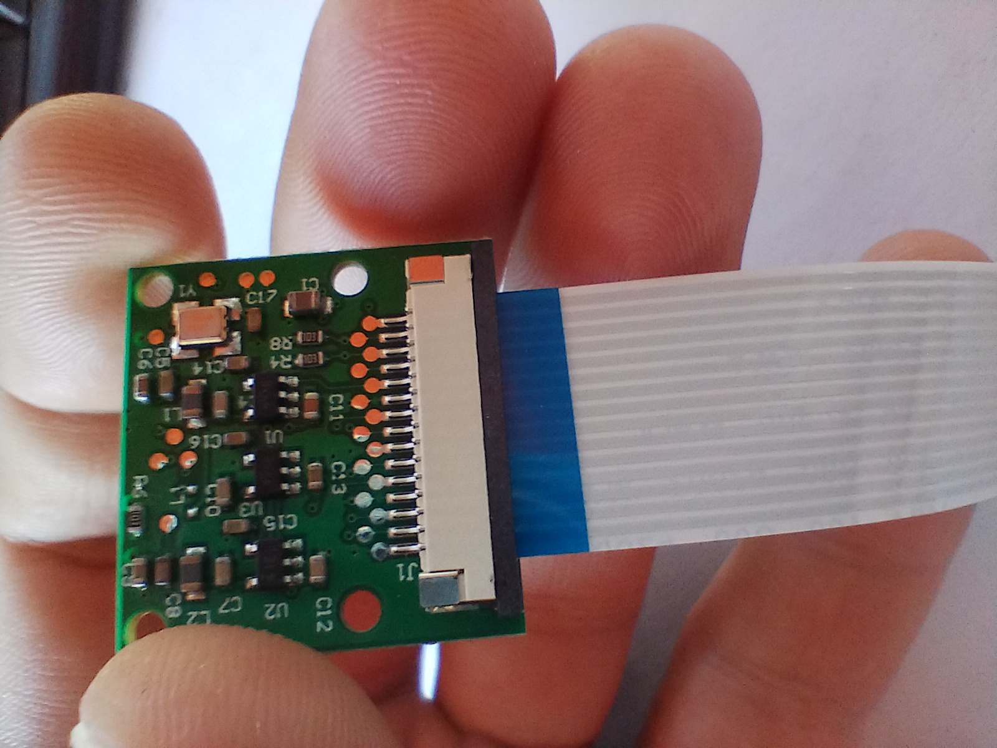
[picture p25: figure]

Figure 1: Standard Raspberry Pi Camera Module V1.3 board.

- Black Plastic Holder: The square plastic glued to the board. It comes with double tape which you have to peel of so yuo can glue it to the board for it to stay at a fixed position. It contains the lens, the IR filter and the sensor.

3

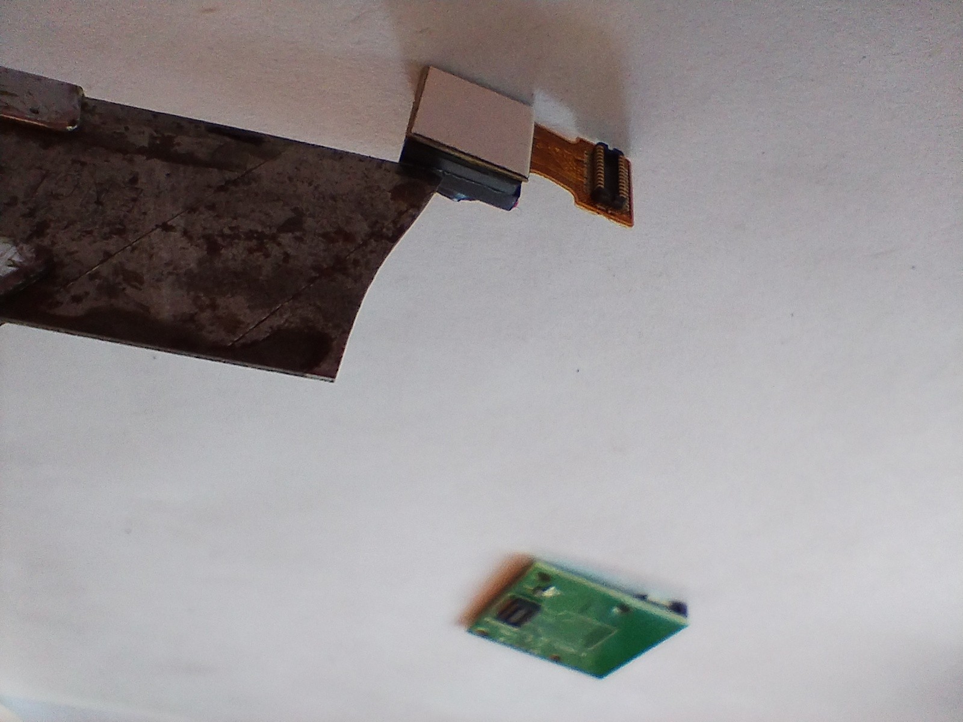
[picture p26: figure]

Figure 2: Plastic holder, containing the sensor and the optical components

- Lens Assembly: The circular, threaded part screwed into the holder.
- IR Filter: A tiny, square piece of glass (often with a greenish or yellowish coating) located inside the black plastic holder, directly above the actual sensor chip. This is your target.

4

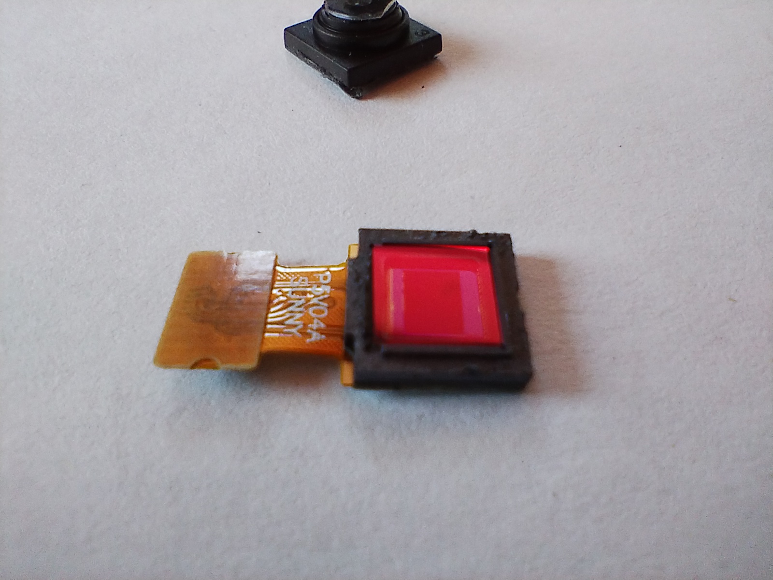
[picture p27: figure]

Figure 3: View of the optical component with the lens removed, exposing the IR filter (redish colour)

Step-by-Step Guide

Step 1: Preparation

Secure the Raspberry Pi Camera board to your workspace using a small amount of adhesive putty or double-sided tape. This prevents the board from slipping while you perform the delicate cuts. Ensure your workspace is as dust-free as possible.

5

Step 2: Unplug the Black Plastic Holder so you can comfortably work on it.
Step 3: Cutting away the Plastic Holder

This is the most critical and dangerous step. Your goal is to separate the black plastic holder from the red circuit board without the knife slipping and destroying the sensor chip underneath.

Use the tip of your scalpel to apply gentle, persistent pressure at one of the corners where the plastic holder meets the red board. The holder is held on by a strong adhesive.

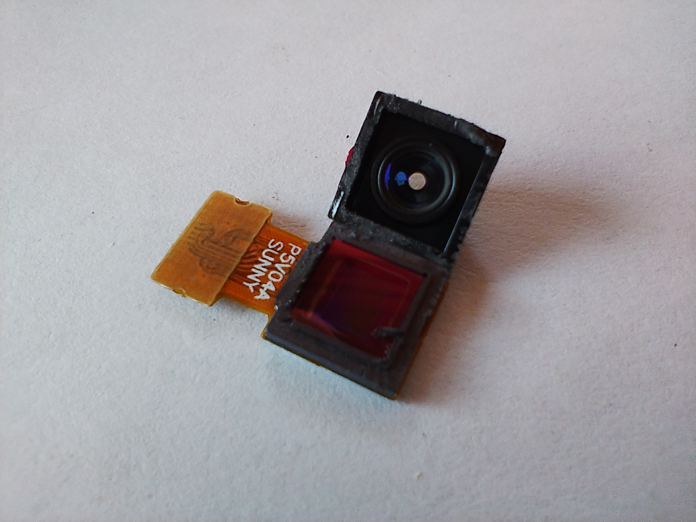
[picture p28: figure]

Figure 4: Applying gentle, persistent pressure with a precision blade at the corner of the black plastic holder.

Continue carefully prying at each corner. Do not rush. You are trying to break the glue’s bond, not cut through the board itself.

6

As the glue starts to give, the holder will lift. Carefully remove it. Do not touch the silver sensor chip exposed on the board.

Step 4: Removing the IR Filter

Now that the holder is removed, look inside it from the bottom (the side that was glued to the board). You will see the tiny, square IR cut-off filter.

Figure 5: Camera with the square IR filter exposed

The filter is typically held in place by a ring of adhesive. Use the very tip of your scalpel to carefully pry the edge of the glass filter.

Apply gentle pressure until the filter pops out of the plastic holder. You can now dispose of the filter.

7

Verification: Ensure no broken glass shards or debris are left inside the plastic holder. Use a clean, soft brush or compressed air to remove any contaminants. Do not blow on it with your mouth.

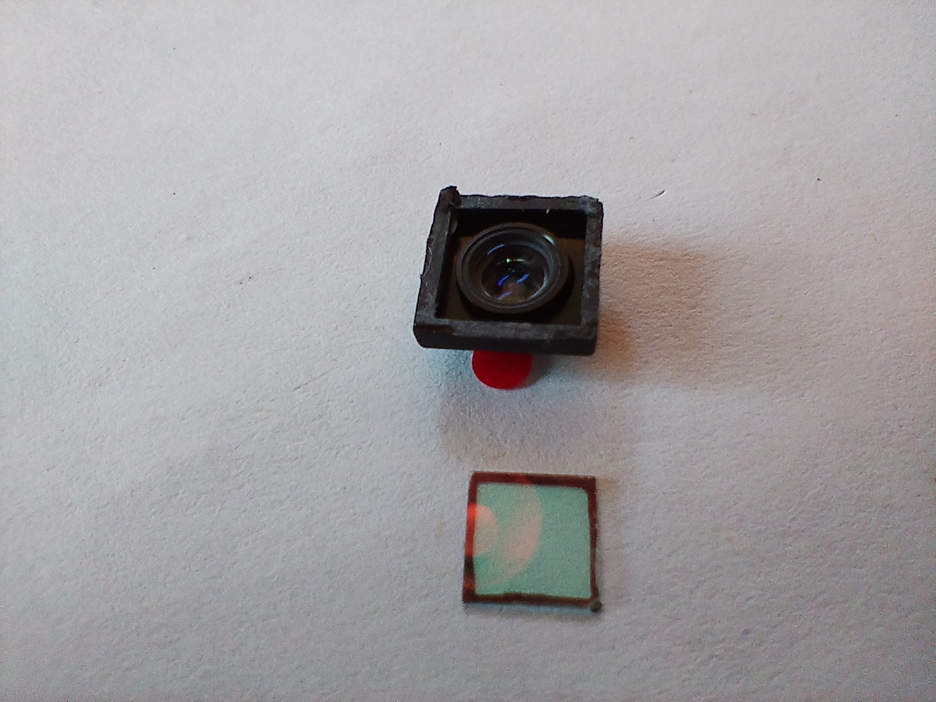
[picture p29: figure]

Figure 6: The successfully removed square glass IR filter alongside the lens assembly.

Step 5: Reassembly

Look closely at the silver sensor chip on the red board. It must be perfectly clean. If there is any debris, very carefully remove it with a clean brush or compressed air. NEVER touch the sensor surface with your fingers, a cloth, or any hard tool.

Mount the sensor back into the board by plugging the connector. Peel of the tape to fix the sensor to the board. At the end, the camera should look like this:

8

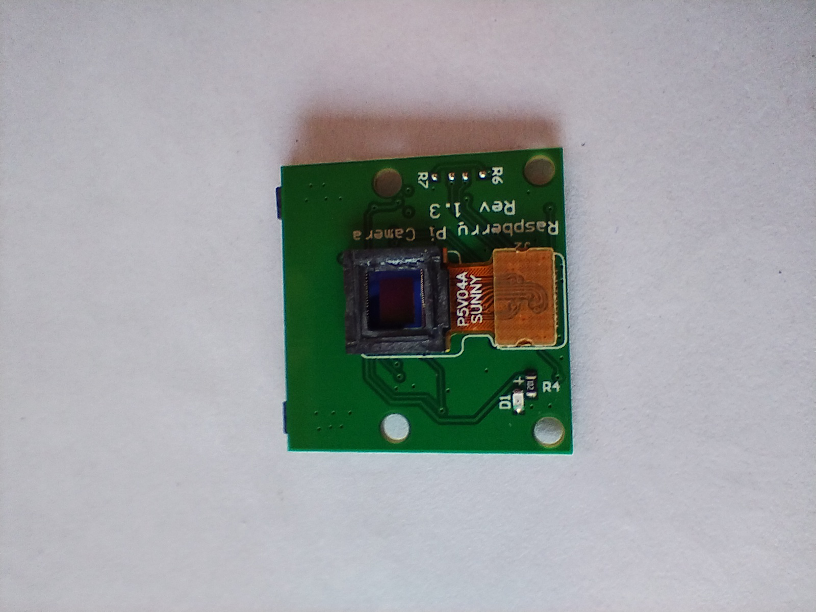
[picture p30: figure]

Figure 7: End result: Sensor was fixed with the tape and ribbon was plugged into the board’s connector during reassembly

When gluing the plastic holder back onto the board, ensure it is perfectly centered over the sensor chip to prevent horizontal spectral offsets in the ImageProcessor.py alignment phase.

Testing Your Modified Camera

Put it inside the Ecophysiometer housing and try taking a photo with the white absorbance LED turned on. You whould be able to see a rainbow:

9


Figure 8: Representative rainbow spectrum captured by the modified sensor inside the housing to verify successful IR filter removal.

10

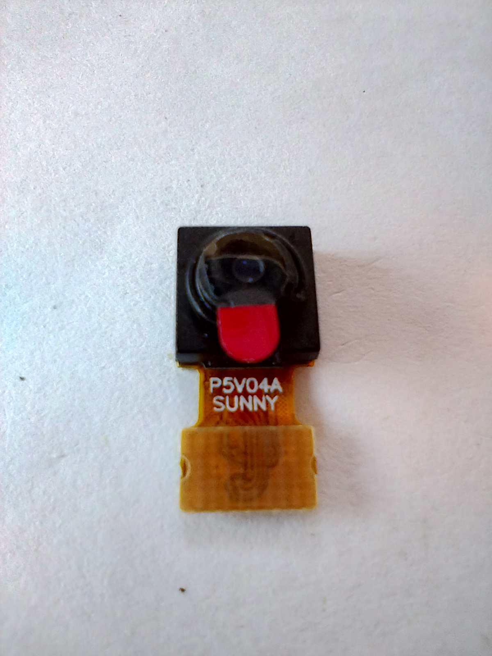
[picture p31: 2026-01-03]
Instructions/IR removal/Photos/3.jpg

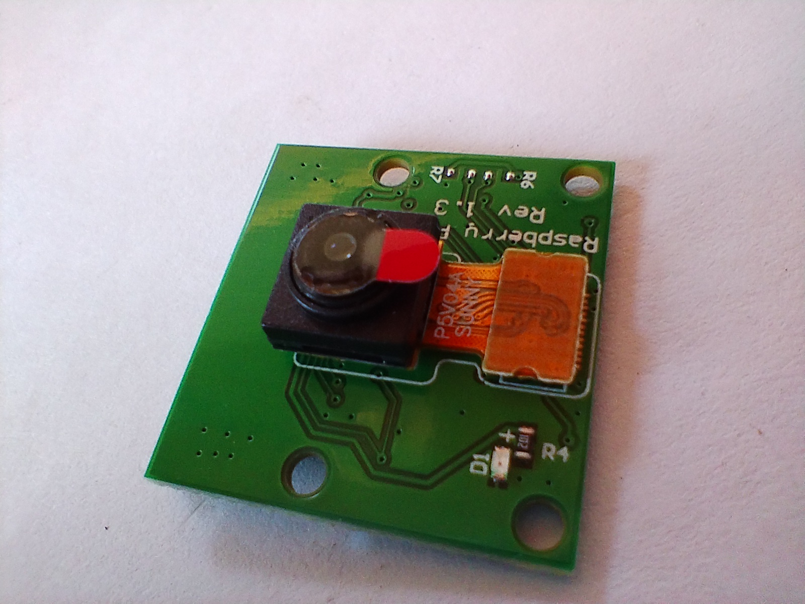
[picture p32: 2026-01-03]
Instructions/IR removal/Photos/2.jpg

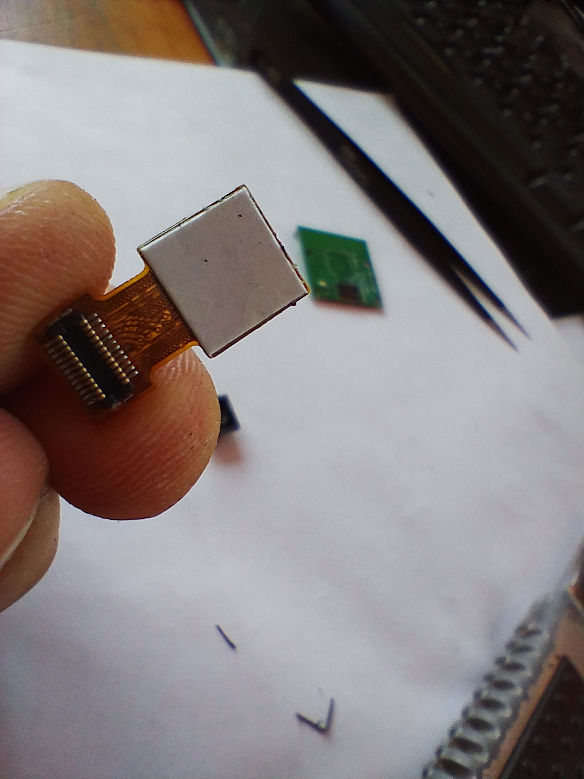
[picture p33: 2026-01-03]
Instructions/IR removal/Photos/8.jpg

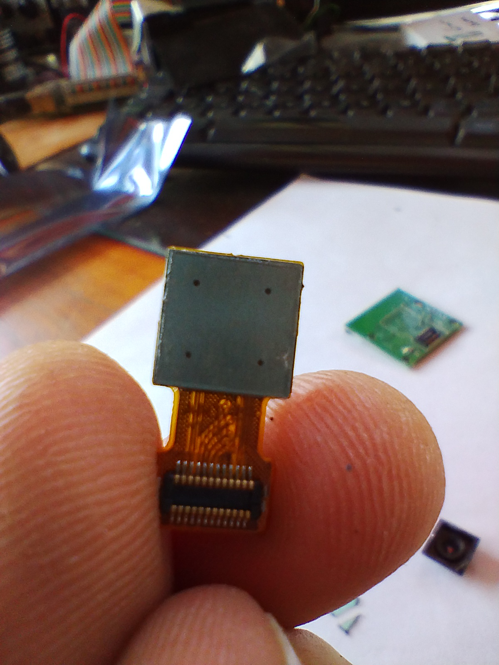
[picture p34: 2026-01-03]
Instructions/IR removal/Photos/9.jpg

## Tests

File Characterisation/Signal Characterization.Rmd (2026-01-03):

---
title: "Sensor response"
author: "Guido Marconi"
date: "`r Sys.Date()`"
output: html_document
---

```{r setup, include=FALSE}
knitr::opts_chunk$set(echo = TRUE)
library(tidyverse)
library(reticulate)
library(gganimate)
renv::use_python()
library(pls)
reticulate::source_python("analize.py")
```

```{python PySetup, include=FALSE}
#import matplotlib as mpl
import numpy as np
#import matplotlib.pyplot as plt
from scipy.signal import correlate
import rawpy
import os

import numpy as np
from scipy.signal import correlate
import rawpy
#from numpy import savetxt
import os

def get_pixel_shift(A, B):
    # regularize datasets by subtracting mean and dividing by s.d.
    A = A - A.mean()
    A = A / A.std()
    B = B - B.mean()
    B = B / B.std()
    xcorr = correlate(A, B)
    # delta time array to match xcorr
    nsamples = A.size
    dt = np.arange(1 - nsamples, nsamples)
    recovered_time_shift = dt[xcorr.argmax()]
    return (recovered_time_shift)
def align_spectra(F):
    size = len(F[:, 0])
    Out = F[:, :]  # select first row
    A = F[0, :]  # select first row
    for i in range(1, size):  # and then iterate through the rest, comparing against the first
        B = F[i, :]
        shift = get_pixel_shift(B, A)
        # calculates the lag between both rows
        Out[i, :] = np.roll(F[i, :],-shift)  # then shifts the row to match both spectra, replacing the spectrum in the original data
    return (Out)

def get_spectrum(pathToPhoto):
    raw = rawpy.imread(pathToPhoto)
    rgb = raw.postprocess(demosaic_algorithm=0,gamma=(1,1), no_auto_bright=True, output_bps=16)
    Signal = rgb[0:450,:,0]+rgb[0:450,:,1]+rgb[0:450,:,2]
    Aligned = align_spectra(Signal)
    SpectrumFull = np.mean(Aligned[:,0:2560],axis=0)
    test = np.reshape(SpectrumFull,(512,5))
    Spectrum = np.mean(test,axis=1)
    return(Spectrum)
```

## Characterising the sensor response curve

There are three parameters that contribute to the signal: the gain on the amplifier, the exposure or shutter time and the actual flux of light. In this section I'll explore these parameters with the goal of achieving a stable signal that responds linearly to changes in light conditions. 

### Light and exposure time:

The first thing to do is to find saturating conditions that allow for subsequent fine tuning. The first experiment consisted on measuring light at increasing exposure times with 10 ms increments, from 10 to 970 ms. This was done with full light intensity and a gain of 1 (default). From visual inspection already it can be seen that between 40 ms and 50 ms the image starts to show burned pixels, thus to saturate. 
 
 40ms 10 ms.
  
 50 ms.
 
 970 ms.
 
 This is confirmed when the spectra are ploted according to the exposure time:

``` {r}
files = paste0("Data/SingalVsTime Long/",list.files("Data/SingalVsTime Long/"))[c(-1,-99)]
expTimes = files %>% str_extract(pattern = regex("[:digit:]+"))
spectra = map(files,py$get_spectrum) %>% bind_cols()
spectra = t(spectra) %>% as_tibble()
colnames(spectra) = 1:512
spectra$expTimes = expTimes
gathered = spectra %>% gather("pixel","signal",1:512)
gathered$expTimes = gathered$expTimes %>% as.numeric()
gathered$pixel = gathered$pixel %>% as.numeric()
ggplot(gathered,aes(pixel,signal)) + geom_line() + transition_states(expTimes) + labs(title = "Exposure time: {closest_state} us") 
```
Now that the saturating conditions were found, the response of the signal to variations in the exposure time can be explored. This was done by measuring the signal at a fixed gain of 1 and full light intensity at 1 ms intervals from 1 to 49 ms.

``` {r}
files = paste0("Data/SignalVsTime2/",list.files("Data/SignalVsTime2/"))#[-1]
expTimes = files %>% str_extract(pattern = regex("[:digit:]+(?=.d)")) %>% as.numeric()
spectra = map(files,py$get_spectrum) %>% bind_cols()
spectra = t(spectra) %>% as_tibble()
colnames(spectra) = 1:512
spectra$expTimes = expTimes
gathered = spectra %>% gather("pixel","signal",1:512)
gathered$expTimes = gathered$expTimes %>% as.numeric()
gathered$pixel = gathered$pixel %>% as.numeric()
ggplot(gathered,aes(pixel,signal)) + geom_line() + transition_states(expTimes) + labs(title = "Exposure time: {closest_state} us") 
```

``` {r}
files = paste0("Data/PWM and time/20000/",list.files("Data/PWM and time/20000/"))
percLight = files %>% str_extract(pattern = regex("(?<=_)([:digit:].[:digit:]+)")) %>% as.numeric()
spectra = map(files,py$get_spectrum) %>% bind_cols()
spectra = t(spectra) %>% as_tibble()
colnames(spectra) = 1:512
spectra$percLight = percLight
gathered = spectra %>% gather("pixel","signal",1:512)
gathered$pixel = gathered$pixel %>% as.numeric()
ggplot(gathered,aes(pixel,signal)) + geom_line() + transition_states(percLight*100) + labs(title = "Exposure time: {closest_state} %") 
ggplot(gathered, aes(pixel,signal,colour = percLight %>% as.factor())) + geom_line()

files = paste0("Data/PWM and time/40000/",list.files("Data/PWM and time/40000/"))
percLight = files %>% str_extract(pattern = regex("(?<=_)([:digit:].[:digit:]+)")) %>% as.numeric()
spectra = map(files,py$get_spectrum) %>% bind_cols()
spectra = t(spectra) %>% as_tibble()
colnames(spectra) = 1:512
spectra$percLight = percLight
gathered = spectra %>% gather("pixel","signal",1:512)
gathered$pixel = gathered$pixel %>% as.numeric()
ggplot(gathered, aes(pixel %>% as.numeric(),signal,colour = percLight %>% as.factor())) + geom_line()
```
``` {r}
files = paste0("Data/SignalVsTimeVsGain/",list.files("Data/SignalVsTimeVsGain/"))
Gains = files %>% str_extract(pattern = regex("[:digit:]")) %>% as.numeric()
expTimes = files %>% str_extract(pattern = regex("[:digit:]+(?=.d)")) %>% as.numeric()
spectra = map(files,py$get_spectrum) %>% bind_cols()
spectra = t(spectra) %>% as_tibble()
colnames(spectra) = 1:512
spectra$expTimes = expTimes
spectra$gains = Gains
spectra = spectra[spectra$expTimes != 0,]
gathered = spectra %>% gather("pixel","signal",1:512)
gathered$expTimes = gathered$expTimes %>% as.numeric()
gathered$pixel = gathered$pixel %>% as.numeric()
gathered$gains = gathered$gains %>% as.factor()
ggplot(gathered,aes(pixel,signal)) + geom_line() + facet_wrap(~gains) + transition_states(expTimes) + labs(title = "Exposure time: {closest_state} us") 
ggplot(gathered[gathered$pixel == 200,],aes(expTimes,signal)) + geom_line() + facet_wrap(~gains)
```

``` {r}
files = paste0("Data/rep/",list.files("Data/rep/"))#[-1]
expTimes = files %>% str_extract(pattern = regex("[:digit:]+(?=.d)")) %>% as.numeric()
spectra = map(files,py$get_spectrum) %>% bind_cols()
spectra = t(spectra) %>% as_tibble()
colnames(spectra) = 1:512
spectra$expTimes = expTimes
gathered = spectra %>% gather("pixel","signal",1:512)
gathered$expTimes = gathered$expTimes %>% as.numeric()
gathered$pixel = gathered$pixel %>% as.numeric()
ggplot(gathered,aes(pixel,signal)) + geom_line() + transition_states(expTimes) + labs(title = "Exposure time: {closest_state} us") 
(apply(spectra, 2, sd)/colMeans(spectra) )%>% .[1:512] %>% plot()
```

``` {r}
library(rjson)

Results = jsonlite::read_json("Data/results.json")
Spectra = Results %>% map(function(x){x[["spectrum"]]})
Tags = Results %>% map(function(x){x[["tag"]]})
Results[[1]][["spectrum"]]

Spectra = Spectra %>% map(function(x){x %>% unlist %>% return()}) %>% unlist() %>% matrix(byrow = TRUE,ncol = 512) %>% as_tibble()
colnames(Spectra) = 1:512
Spectra$Tag = Tags %>% map(function(x){x %>% unlist %>% return()}) %>% unlist()
Spectra = separate(Spectra,Tag,into = c("camera","light","percent"),sep = "-")
GatheredSpectra = gather(Spectra,"pixel","Value",1:512)

GatheredSpectra$pixel = as.numeric(GatheredSpectra$pixel)
GatheredSpectra$percent = as.numeric(GatheredSpectra$percent)
GatheredSpectra$camera = as.factor(GatheredSpectra$camera)
GatheredSpectra$light = as.factor(GatheredSpectra$light)
#filter(GatheredSpectra,camera == 1) %>% ggplot(aes(pixel,Value,colour = light)) + geom_line() #+ facet_wrap(~light)

GatheredSpectra %>% ggplot(aes(pixel,Value,colour = percent %>% as.factor())) + geom_line() + facet_grid(rows = vars(light),cols = vars(camera))
```

``` {r}
#PercMean = Spectra %>% group_by(percent) %>% select(-camera,-light) %>%  summarise_all(mean)
#gather(PercMean,pixel,value,2:513) %>% ggplot(aes(pixel %>% as.numeric(),value %>% as.numeric(),colour = as.factor(percent))) + geom_line()

filter(GatheredSpectra,camera == 1,light == 1,pixel == 300) %>% ggplot(aes(Value,percent)) + geom_line() 
nestedSpectra = Spectra %>% group_by(light,camera) %>% nest()
library(pls)
PLSR = function(x){
  model = pls::plsr(percent ~ ., data = x, ncomp = 1, validation = "LOO")
  return(model)
}
models = nestedSpectra$data %>% map(PLSR)
par(mfrow= c(2,5))
for(i in 1:10){
  plot(models[[i]])
}
par(mfrow= c(1,1))
```

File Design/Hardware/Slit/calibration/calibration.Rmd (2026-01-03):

---
title: "Analysis of slit width"
author: "Guido"
date: '2022-09-08'
output: html_document
---
```{r}
library(tidyverse)
library(car)
```
The following experiment was performed to assess the feasiblity of manufacturing the slits with the 3d printer Creality Ender 3 V2 in a repetible fashion. The first problem to be asnwered was what is the minimum width that can be printed. There is mismatch between what is explicited in the design and the real output that is caused by many factors such as the limitations of the printer, expansion and contraction of the extruded plastic, etc. Because of this the printer was "calibrated" to learn: the minimum width that can be printed in a reproducible way, the relationship between design parameters and printed output. To this end a plate with slits of different widths between 80 and 1000 um was designed in freecad (n = 22). The printing parameters were specified in the corresponding m3f file. 10 replicates of the plates were printed at different times using PETG as print material (grilon). The slits' were micrographed with a Leica microscope at 10X and widths at the middle of the grooves were measured with a Fiji. Observations: 

- Micrographs of one of the replicates were tilted and slightly out of focus. This resulted in the imposibility of imposibility of measuring distances in a reproducible way. Because of this they were discarded. 

- From all the widths tested, just the largest 13 resulted in non zero sized grooves.

- As the width of the slit decreased, the length did the same. The original design was 5 mm and the slimmest grooves wad a length of around 3 mm. This makes emphasises the need to increase the design spec. from 3 to 5 mm in order to compensate for eventual shrinkage. 

```{r include=FALSE}
Width = c(1000,950,900,850,750,700,650,600,550,500,450,400,350,300,250,200,150,100,95,90,85,80)
measMedDir = list.files("resultados/medio/")
measMedDir = paste("resultados/medio/",measMedDir,sep = "")
measMedDir = measMedDir[-1]
med = map(measMedDir,read_csv)
med %>% map(nrow) %>% unlist() %>% table()
med = map(med,function(x){if(nrow(x)<13){rbind(rep(0,7),x)}else {x}})
med %>% map(nrow) %>% unlist() %>% table()
Width = Width[1:13] %>% sort()
med = map(med,select,Length) %>% map(mutate, width = Width)
med = lapply(1:length(med), function(x){med[[x]]%>% mutate(slitN = x)}) %>% bind_rows()
med$slitN = med$slitN %>% as.factor() 
```
As can be seen in the graphs there is a systematic mismatch between the design specification and the resulting width. The smallest specification (350 um) resulted in a closed groove in 4 out of 9 replicas. This reflects not only on the trend, but also in a higher variance. This already indicates a lower boundary at which the fabrication technique looses reproducibility. Because of this, all measurements corresponding to this widths were discarded for future analyses. The variability in the width produced by the fabrication technique is equal regardless of the size of the hole as proved by the levene test 

```{r}
medByPWidth = med %>% group_by(width) %>% summarise(mean = mean(Length),sd = sd(Length))
ggplot(medByPWidth,aes(width,mean)) + geom_point(size = 2) + geom_errorbar(aes(ymin=mean-sd, ymax=mean+sd), width = 0.05) +  geom_rect(aes(xmin = 325, xmax = 375, ymin = -20, ymax = 150), 
            fill = "red", alpha = 0.05)
medSelect = med[med$width > 350,]
leveneTest(medSelect$Length,medSelect$width)
```
As can be seen by the plot and explored by a model. The fabrication technique is fairly reproducible, yielding in comparable mean widths. The residuals didn't have normal distribution so a Kruskal-Wallis test was applied
```{r}
ggplot(med,aes(slitN,Length)) + geom_boxplot()
group = lm(Length ~ slitN,data = medSelect)
group %>% summary()
par(mfrow =c(2,2) )
group %>% plot()
shapiro.test(group$residuals)
group = kruskal.test(Length ~ slitN,data = medSelect)
group
```
To assess the functional relation between the design specification and output, a series of linear models were built and evaluated. The final model was built using a 3rd degree polynomial because it met all assumptions of LM and had the lowest AIC. 

first degree has a pattern in the residuals with a parabolic shape, indicating the need for a sqare term.
```{r}

ggplot(medSelect,aes(width,Length)) + geom_point() 
poly1 = lm(Length ~ poly(width,1),data = medSelect)
poly1 %>% summary()
par(mfrow =c(2,2) )
poly1 %>% plot()
```

In the case of the 2nd degree it exhibited an s shape parameter with 3 intercepts, indicating that a 3rd order term may be necesary.

```{r}
poly2 = lm(Length ~ poly(width,2),data = medSelect)
poly2 %>% summary()
par(mfrow =c(2,2) )
poly2 %>% plot()
```
Finally, we are there

```{r}

poly3 = lm(Length ~ poly(width,3),data = medSelect)
poly3 %>% summary()
par(mfrow =c(2,2) )
poly3 %>% plot()
poly3$residuals %>% leveneTest(medSelect$width)
poly3$residuals %>% shapiro.test()
AIC(poly1,poly2,poly3)
ggplot(data = medSelect,aes(width,Length)) + geom_point() + geom_smooth(method="lm",formula = y ~ poly(x,3)) + ylab("Real Width (um)") + xlab("Predicted width (um)") + geom_text(aes(x = 500 ,y = 750 ,label = "R² = 0.9868")) 
```

Now, the reverse model is built to predict the design specification needed to achieve a desired width. Despite the model has a standard error of prediction of 22.22 um, the experimental data suggest that that may be an overly optimistic estimate.
```{r}

reversed = lm(width ~ poly(Length,3),data = medSelect)
reversed %>% summary()
par(mfrow =c(2,2) )
reversed %>% plot()
```
To avoid being too close to the lowest value and taking into account the standard error, a width that has good chances of working could be a value in between those resulting for a specification of 400 um and 450 um. The resulting specification will be 424 um

```{r}
aim = medSelect[medSelect$width < 451,1] %>% unlist() %>% mean()
predict(reversed,tibble(Length = 200)) %>% round()
```
To test the results, a pull of 20 plates were printed. From the first to this experiment, the plastic was used from a different batch and the plate was re-leveled. From the pull, 16 had open slits. Out of these 16, only 13 resulted in truly viable options since 3 presented small imperfections such as small obstruction of the light path or a sudden increase in the width. None the less, their values were used for statistics. The equality in means between the value predicted with the model and the final result proves that the printer can be used to manufacture the plates. The only observation worth mentioning is the results were more variable than the results used for the claibration.
```{r}
resultados = read_csv("resultados/resultados.csv")
resultados$Length %>% summary()
ggplot(resultados,aes(Length)) + geom_histogram(aes(y =..density..),binwidth = 21) +
  stat_function(fun = dnorm, args = list(mean = mean(resultados$Length), sd = sd(resultados$Length)))+ geom_vline(aes(xintercept = 200,colour = "Desired width"))+ geom_vline(aes(xintercept = mean(resultados$Length),colour = "Result")) + xlab(label = "Width (um)") + geom_text(aes(x = 250, y = 0.01,label = "p val = 0.7952"))
resultados$Length %>% shapiro.test()
resultados$Length %>% sd()
t.test(resultados$Length,mu = 200)
sd(resultados$Length)/mean(resultados$Length) 

var.test(resultados$Length,reversed$residuals)
```

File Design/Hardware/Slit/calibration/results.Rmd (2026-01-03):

---
title: "Analysis of slit width"
output: html_notebook
---

```{r}
library(tidyverse)
library(car)
```
```{r}
Width = c(1000,950,900,850,750,700,650,600,550,500,450,400,350,300,250,200,150,100,95,90,85,80)
measMedDir = list.files("resultados/medio/")
measMedDir = paste("resultados/medio/",measMedDir,sep = "")
med = map(measMedDir,read_csv)
med %>% map(nrow) %>% unlist() %>% table()
med = map(med,function(x){if(nrow(x)<13){rbind(rep(0,7),x)}else {x}})
med %>% map(nrow) %>% unlist() %>% table()
Width = Width[1:13] %>% sort()
med = map(med,select,Length) %>% map(mutate, width = Width)
med = lapply(1:length(med), function(x){med[[x]]%>% mutate(slitN = x)}) %>% bind_rows()
med$slitN = med$slitN %>% as.factor() 
```

```{r}
medByPWidth = med %>% group_by(width) %>% summarise(mean = mean(Length),sd = sd(Length))
ggplot(medByPWidth,aes(width,mean)) + geom_point(size = 2) + geom_errorbar(aes(ymin=mean-sd, ymax=mean+sd), width = 0.05) +  geom_rect(aes(xmin = 325, xmax = 375, ymin = -20, ymax = 150), 
            fill = "red", alpha = 0.05)
ggplot(med,aes(slitN,Length)) + geom_boxplot()
leveneTest(medSelect$Length,medSelect$width)
```

```{r}
medSelect = med[med$width > 350,]
ggplot(medSelect,aes(width,Length)) + geom_point() 
poly1 = lm(Length ~ poly(width,1),data = medSelect)
poly1 %>% summary()
poly1 %>% plot()
```
```{r}
poly2 = lm(Length ~ poly(width,2),data = medSelect)
poly2 %>% summary()
poly2 %>% plot()
```
```{r}

poly3 = lm(Length ~ poly(width,3),data = medSelect)
poly3 %>% summary()
poly3 %>% plot()
poly3$residuals %>% leveneTest(medSelect$width)
AIC(poly1,poly2,poly3)
```
```{r}

reversed = lm(width ~ poly(Length,3),data = medSelect)
reversed %>% summary()
reversed %>% plot()
```

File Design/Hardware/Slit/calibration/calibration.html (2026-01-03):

# Analysis of slit width

#### Guido

#### 2022-09-08

library(tidyverse)

## ── Attaching packages ─────────────────────────────────────── tidyverse 1.3.1 ──

## ✔ ggplot2 3.3.6     ✔ purrr   0.3.4
## ✔ tibble  3.1.7     ✔ dplyr   1.0.9
## ✔ tidyr   1.2.0     ✔ stringr 1.4.0
## ✔ readr   2.1.2     ✔ forcats 0.5.1

## ── Conflicts ────────────────────────────────────────── tidyverse_conflicts() ──
## ✖ dplyr::filter() masks stats::filter()
## ✖ dplyr::lag()    masks stats::lag()

library(car)

## Loading required package: carData

## 
## Attaching package: 'car'

## The following object is masked from 'package:dplyr':
## 
##     recode

## The following object is masked from 'package:purrr':
## 
##     some

The following experiment was performed to assess the feasiblity of manufacturing the slits with the 3d printer Creality Ender 3 V2 in a repetible fashion. The first problem to be asnwered was what is the minimum width that can be printed. There is mismatch between what is explicited in the design and the real output that is caused by many factors such as the limitations of the printer, expansion and contraction of the extruded plastic, etc. Because of this the printer was “calibrated” to learn: the minimum width that can be printed in a reproducible way, the relationship between design parameters and printed output. To this end a plate with slits of different widths between 80 and 1000 um was designed in freecad (n = 22). The printing parameters were specified in the corresponding m3f file. 10 replicates of the plates were printed at different times using PETG as print material (grilon). The slits’ were micrographed with a Leica microscope at 10X and widths at the middle of the grooves were measured with a Fiji. Observations:

- Micrographs of one of the replicates were tilted and slightly out of focus. This resulted in the imposibility of imposibility of measuring distances in a reproducible way. Because of this they were discarded.
- From all the widths tested, just the largest 13 resulted in non zero sized grooves.

As can be seen in the graphs there is a systematic mismatch between the design specification and the resulting width. The smallest specification (350 um) resulted in a closed groove in 4 out of 9 replicas. This reflects not only on the trend, but also in a higher variance. This already indicates a lower boundary at which the fabrication technique looses reproducibility. Because of this, all measurements corresponding to this widths were discarded for future analyses. The variability in the width produced by the fabrication technique is equal regardless of the size of the hole as proved by the levene test

medByPWidth = med %>% group_by(width) %>% summarise(mean = mean(Length),sd = sd(Length))
ggplot(medByPWidth,aes(width,mean)) + geom_point(size = 2) + geom_errorbar(aes(ymin=mean-sd, ymax=mean+sd), width = 0.05) +  geom_rect(aes(xmin = 325, xmax = 375, ymin = -20, ymax = 150), 
            fill = "red", alpha = 0.05)

medSelect = med[med$width > 350,]
leveneTest(medSelect$Length,medSelect$width)

## Warning in leveneTest.default(medSelect$Length, medSelect$width):
## medSelect$width coerced to factor.

## Levene's Test for Homogeneity of Variance (center = median)
##       Df F value Pr(>F)
## group 11  0.4321  0.938
##       96

As can be seen by the plot and explored by a model. The fabrication technique is fairly reproducible, yielding in comparable mean widths. The residuals didn’t have normal distribution so a Kruskal-Wallis test was applied

ggplot(med,aes(slitN,Length)) + geom_boxplot()

group = lm(Length ~ slitN,data = medSelect)
group %>% summary()

## 
## Call:
## lm(formula = Length ~ slitN, data = medSelect)
## 
## Residuals:
##     Min      1Q  Median      3Q     Max 
## -353.87 -213.80  -49.07  195.57  500.53 
## 
## Coefficients:
##             Estimate Std. Error t value Pr(>|t|)    
## (Intercept) 529.5995    76.2206   6.948 3.96e-10 ***
## slitN2       29.3332   107.7922   0.272    0.786    
## slitN3      -43.4667   107.7922  -0.403    0.688    
## slitN4        0.9332   107.7922   0.009    0.993    
## slitN5      -10.4000   107.7922  -0.096    0.923    
## slitN6        9.7332   107.7922   0.090    0.928    
## slitN7      -20.5333   107.7922  -0.190    0.849    
## slitN8       33.5999   107.7922   0.312    0.756    
## slitN9      -19.3333   107.7922  -0.179    0.858    
## ---
## Signif. codes:  0 '***' 0.001 '**' 0.01 '*' 0.05 '.' 0.1 ' ' 1
## 
## Residual standard error: 264 on 99 degrees of freedom
## Multiple R-squared:  0.008333,   Adjusted R-squared:  -0.0718 
## F-statistic: 0.104 on 8 and 99 DF,  p-value: 0.999

par(mfrow =c(2,2) )
group %>% plot()

shapiro.test(group$residuals)

## 
##  Shapiro-Wilk normality test
## 
## data:  group$residuals
## W = 0.9309, p-value = 2.876e-05

group = kruskal.test(Length ~ slitN,data = medSelect)
group

## 
##  Kruskal-Wallis rank sum test
## 
## data:  Length by slitN
## Kruskal-Wallis chi-squared = 1.2705, df = 8, p-value = 0.9959

To assess the functional relation between the design specification and output, a series of linear models were built and evaluated. The final model was built using a 3rd degree polynomial because it met all assumptions of LM and had the lowest AIC.

first degree has a pattern in the residuals with a parabolic shape, indicating the need for a sqare term.

ggplot(medSelect,aes(width,Length)) + geom_point()

poly1 = lm(Length ~ poly(width,1),data = medSelect)
poly1 %>% summary()

## 
## Call:
## lm(formula = Length ~ poly(width, 1), data = medSelect)
## 
## Residuals:
##     Min      1Q  Median      3Q     Max 
## -81.744 -32.894  -4.301  26.253 114.489 
## 
## Coefficients:
##                Estimate Std. Error t value Pr(>|t|)    
## (Intercept)     527.362      4.038  130.60   <2e-16 ***
## poly(width, 1) 2602.522     41.962   62.02   <2e-16 ***
## ---
## Signif. codes:  0 '***' 0.001 '**' 0.01 '*' 0.05 '.' 0.1 ' ' 1
## 
## Residual standard error: 41.96 on 106 degrees of freedom
## Multiple R-squared:  0.9732, Adjusted R-squared:  0.9729 
## F-statistic:  3847 on 1 and 106 DF,  p-value: < 2.2e-16

par(mfrow =c(2,2) )
poly1 %>% plot()

In the case of the 2nd degree it exhibited an s shape parameter with 3 intercepts, indicating that a 3rd order term may be necesary.

poly2 = lm(Length ~ poly(width,2),data = medSelect)
poly2 %>% summary()

## 
## Call:
## lm(formula = Length ~ poly(width, 2), data = medSelect)
## 
## Residuals:
##     Min      1Q  Median      3Q     Max 
## -83.301 -21.165   0.785  20.523  66.217 
## 
## Coefficients:
##                 Estimate Std. Error t value Pr(>|t|)    
## (Intercept)       527.36       2.84  185.66   <2e-16 ***
## poly(width, 2)1  2602.52      29.52   88.17   <2e-16 ***
## poly(width, 2)2   308.48      29.52   10.45   <2e-16 ***
## ---
## Signif. codes:  0 '***' 0.001 '**' 0.01 '*' 0.05 '.' 0.1 ' ' 1
## 
## Residual standard error: 29.52 on 105 degrees of freedom
## Multiple R-squared:  0.9869, Adjusted R-squared:  0.9866 
## F-statistic:  3941 on 2 and 105 DF,  p-value: < 2.2e-16

par(mfrow =c(2,2) )
poly2 %>% plot()

Finally, we are there

poly3 = lm(Length ~ poly(width,3),data = medSelect)
poly3 %>% summary()

## 
## Call:
## lm(formula = Length ~ poly(width, 3), data = medSelect)
## 
## Residuals:
##     Min      1Q  Median      3Q     Max 
## -73.011 -19.415   1.357  18.066  50.710 
## 
## Coefficients:
##                 Estimate Std. Error t value Pr(>|t|)    
## (Intercept)      527.362      2.689 196.099  < 2e-16 ***
## poly(width, 3)1 2602.522     27.948  93.121  < 2e-16 ***
## poly(width, 3)2  308.475     27.948  11.038  < 2e-16 ***
## poly(width, 3)3  101.299     27.948   3.625  0.00045 ***
## ---
## Signif. codes:  0 '***' 0.001 '**' 0.01 '*' 0.05 '.' 0.1 ' ' 1
## 
## Residual standard error: 27.95 on 104 degrees of freedom
## Multiple R-squared:  0.9883, Adjusted R-squared:  0.988 
## F-statistic:  2936 on 3 and 104 DF,  p-value: < 2.2e-16

par(mfrow =c(2,2) )
poly3 %>% plot()

poly3$residuals %>% leveneTest(medSelect$width)

## Warning in leveneTest.default(., medSelect$width): medSelect$width coerced to
## factor.

## Levene's Test for Homogeneity of Variance (center = median)
##       Df F value Pr(>F)
## group 11  0.4321  0.938
##       96

poly3$residuals %>% shapiro.test()

## 
##  Shapiro-Wilk normality test
## 
## data:  .
## W = 0.9852, p-value = 0.2774

AIC(poly1,poly2,poly3)

##       df      AIC
## poly1  3 1117.615
## poly2  4 1042.614
## poly3  5 1031.767

Now, the reverse model is built to predict the design specification needed to achieve a desired width. Despite the model has a standard error of prediction of 22.22 um, the experimental data suggest that that may be an overly optimistic estimate.

reversed = lm(width ~ poly(Length,3),data = medSelect)
reversed %>% summary()

## 
## Call:
## lm(formula = width ~ poly(Length, 3), data = medSelect)
## 
## Residuals:
##     Min      1Q  Median      3Q     Max 
## -52.208 -12.127   0.378  13.262  55.424 
## 
## Coefficients:
##                  Estimate Std. Error t value Pr(>|t|)    
## (Intercept)       691.667      2.138  323.51  < 2e-16 ***
## poly(Length, 3)1 1972.383     22.219   88.77  < 2e-16 ***
## poly(Length, 3)2 -228.442     22.219  -10.28  < 2e-16 ***
## poly(Length, 3)3  -60.653     22.219   -2.73  0.00744 ** 
## ---
## Signif. codes:  0 '***' 0.001 '**' 0.01 '*' 0.05 '.' 0.1 ' ' 1
## 
## Residual standard error: 22.22 on 104 degrees of freedom
## Multiple R-squared:  0.9872, Adjusted R-squared:  0.9868 
## F-statistic:  2664 on 3 and 104 DF,  p-value: < 2.2e-16

par(mfrow =c(2,2) )
reversed %>% plot()

To avoid being too close to the lowest value and taking into account the standard error, a width that has good chances of working could be a value in between those resulting for a specification of 400 um and 450 um. The resulting specification will be 424 um

aim = medSelect[medSelect$width < 451,1] %>% unlist() %>% mean()
predict(reversed,tibble(Length = 200)) %>% round()

##   1 
## 424

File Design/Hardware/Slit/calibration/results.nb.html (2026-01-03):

Code

- Show All Code
- Hide All Code
- Download Rmd

# Analysis of slit width

library(car)

Loading required package: carData

Attaching package: ‘car’

The following object is masked from ‘package:dplyr’:

    recode

The following object is masked from ‘package:purrr’:

    some

Width = c(1000,950,900,850,750,700,650,600,550,500,450,400,350,300,250,200,150,100,95,90,85,80)
measMedDir = list.files("resultados/medio/")
measMedDir = paste("resultados/medio/",measMedDir,sep = "")
med = map(measMedDir,read_csv)

New names:
• `` -> `...1`
Rows: 12 Columns: 7
── Column specification ───────────────────────────────────────────────────────────────────────────────────
Delimiter: ","
dbl (7): ...1, Area, Mean, Min, Max, Angle, Length

ℹ Use `spec()` to retrieve the full column specification for this data.
ℹ Specify the column types or set `show_col_types = FALSE` to quiet this message.
New names:
• `` -> `...1`
Rows: 12 Columns: 7
── Column specification ───────────────────────────────────────────────────────────────────────────────────
Delimiter: ","
dbl (7): ...1, Area, Mean, Min, Max, Angle, Length

ℹ Use `spec()` to retrieve the full column specification for this data.
ℹ Specify the column types or set `show_col_types = FALSE` to quiet this message.
New names:
• `` -> `...1`
Rows: 13 Columns: 7
── Column specification ───────────────────────────────────────────────────────────────────────────────────
Delimiter: ","
dbl (7): ...1, Area, Mean, Min, Max, Angle, Length

ℹ Use `spec()` to retrieve the full column specification for this data.
ℹ Specify the column types or set `show_col_types = FALSE` to quiet this message.
New names:
• `` -> `...1`
Rows: 12 Columns: 7
── Column specification ───────────────────────────────────────────────────────────────────────────────────
Delimiter: ","
dbl (7): ...1, Area, Mean, Min, Max, Angle, Length

ℹ Use `spec()` to retrieve the full column specification for this data.
ℹ Specify the column types or set `show_col_types = FALSE` to quiet this message.
New names:
• `` -> `...1`
Rows: 12 Columns: 7
── Column specification ───────────────────────────────────────────────────────────────────────────────────
Delimiter: ","
dbl (7): ...1, Area, Mean, Min, Max, Angle, Length

ℹ Use `spec()` to retrieve the full column specification for this data.
ℹ Specify the column types or set `show_col_types = FALSE` to quiet this message.
New names:
• `` -> `...1`
Rows: 13 Columns: 7
── Column specification ───────────────────────────────────────────────────────────────────────────────────
Delimiter: ","
dbl (7): ...1, Area, Mean, Min, Max, Angle, Length

ℹ Use `spec()` to retrieve the full column specification for this data.
ℹ Specify the column types or set `show_col_types = FALSE` to quiet this message.
New names:
• `` -> `...1`
Rows: 13 Columns: 7
── Column specification ───────────────────────────────────────────────────────────────────────────────────
Delimiter: ","
dbl (7): ...1, Area, Mean, Min, Max, Angle, Length

ℹ Use `spec()` to retrieve the full column specification for this data.
ℹ Specify the column types or set `show_col_types = FALSE` to quiet this message.
New names:
• `` -> `...1`
Rows: 13 Columns: 7
── Column specification ───────────────────────────────────────────────────────────────────────────────────
Delimiter: ","
dbl (7): ...1, Area, Mean, Min, Max, Angle, Length

ℹ Use `spec()` to retrieve the full column specification for this data.
ℹ Specify the column types or set `show_col_types = FALSE` to quiet this message.
New names:
• `` -> `...1`
Rows: 13 Columns: 7
── Column specification ───────────────────────────────────────────────────────────────────────────────────
Delimiter: ","
dbl (7): ...1, Area, Mean, Min, Max, Angle, Length

ℹ Use `spec()` to retrieve the full column specification for this data.
ℹ Specify the column types or set `show_col_types = FALSE` to quiet this message.
New names:
• `` -> `...1`
Rows: 12 Columns: 7
── Column specification ───────────────────────────────────────────────────────────────────────────────────
Delimiter: ","
dbl (7): ...1, Area, Mean, Min, Max, Angle, Length

ℹ Use `spec()` to retrieve the full column specification for this data.
ℹ Specify the column types or set `show_col_types = FALSE` to quiet this message.

med %>% map(nrow) %>% unlist() %>% table()

.
12 13 
 5  5

med = map(med,function(x){if(nrow(x)<13){rbind(rep(0,7),x)}else {x}})
med %>% map(nrow) %>% unlist() %>% table()

.
13 
10

Width = Width[1:13] %>% sort()

```{r}

Error: attempt to use zero-length variable name

poly3$residuals %>% leveneTest(medSelect$width)

Warning in leveneTest.default(., medSelect$width) :
  medSelect$width coerced to factor.

Levene's Test for Homogeneity of Variance (center = median)
       Df F value Pr(>F)
group  11  0.1906 0.9978
      108

LS0tCnRpdGxlOiAiQW5hbHlzaXMgb2Ygc2xpdCB3aWR0aCIKb3V0cHV0OiBodG1sX25vdGVib29rCi0tLQoKCmBgYHtyfQpsaWJyYXJ5KHRpZHl2ZXJzZSkKbGlicmFyeShjYXIpCmBgYApgYGB7cn0KV2lkdGggPSBjKDEwMDAsOTUwLDkwMCw4NTAsNzUwLDcwMCw2NTAsNjAwLDU1MCw1MDAsNDUwLDQwMCwzNTAsMzAwLDI1MCwyMDAsMTUwLDEwMCw5NSw5MCw4NSw4MCkKbWVhc01lZERpciA9IGxpc3QuZmlsZXMoInJlc3VsdGFkb3MvbWVkaW8vIikKbWVhc01lZERpciA9IHBhc3RlKCJyZXN1bHRhZG9zL21lZGlvLyIsbWVhc01lZERpcixzZXAgPSAiIikKbWVkID0gbWFwKG1lYXNNZWREaXIscmVhZF9jc3YpCm1lZCAlPiUgbWFwKG5yb3cpICU+JSB1bmxpc3QoKSAlPiUgdGFibGUoKQptZWQgPSBtYXAobWVkLGZ1bmN0aW9uKHgpe2lmKG5yb3coeCk8MTMpe3JiaW5kKHJlcCgwLDcpLHgpfWVsc2Uge3h9fSkKbWVkICU+JSBtYXAobnJvdykgJT4lIHVubGlzdCgpICU+JSB0YWJsZSgpCldpZHRoID0gV2lkdGhbMToxM10gJT4lIHNvcnQoKQptZWQgPSBtYXAobWVkLHNlbGVjdCxMZW5ndGgpICU+JSBtYXAobXV0YXRlLCB3aWR0aCA9IFdpZHRoKQptZWQgPSBsYXBwbHkoMTpsZW5ndGgobWVkKSwgZnVuY3Rpb24oeCl7bWVkW1t4XV0lPiUgbXV0YXRlKHNsaXROID0geCl9KSAlPiUgYmluZF9yb3dzKCkKbWVkJHNsaXROID0gbWVkJHNsaXROICU+JSBhcy5mYWN0b3IoKSAKYGBgCgpgYGB7cn0KbWVkQnlQV2lkdGggPSBtZWQgJT4lIGdyb3VwX2J5KHdpZHRoKSAlPiUgc3VtbWFyaXNlKG1lYW4gPSBtZWFuKExlbmd0aCksc2QgPSBzZChMZW5ndGgpKQpnZ3Bsb3QobWVkQnlQV2lkdGgsYWVzKHdpZHRoLG1lYW4pKSArIGdlb21fcG9pbnQoc2l6ZSA9IDIpICsgZ2VvbV9lcnJvcmJhcihhZXMoeW1pbj1tZWFuLXNkLCB5bWF4PW1lYW4rc2QpLCB3aWR0aCA9IDAuMDUpICsgIGdlb21fcmVjdChhZXMoeG1pbiA9IDMyNSwgeG1heCA9IDM3NSwgeW1pbiA9IC0yMCwgeW1heCA9IDE1MCksIAogICAgICAgICAgICBmaWxsID0gInJlZCIsIGFscGhhID0gMC4wNSkKZ2dwbG90KG1lZCxhZXMoc2xpdE4sTGVuZ3RoKSkgKyBnZW9tX2JveHBsb3QoKQpgYGAKCmBgYHtyfQptZWRTZWxlY3QgPSBtZWRbbWVkJHdpZHRoID4gMzUwLF0KZ2dwbG90KG1lZFNlbGVjdCxhZXMod2lkdGgsTGVuZ3RoKSkgKyBnZW9tX3BvaW50KCkgCnBvbHkxID0gbG0oTGVuZ3RoIH4gcG9seSh3aWR0aCwxKSxkYXRhID0gbWVkU2VsZWN0KQpwb2x5MSAlPiUgc3VtbWFyeSgpCnBvbHkxICU+JSBwbG90KCkKYGBgCmBgYHtyfQptZWRTZWxlY3QgPSBtZWRbbWVkJHdpZHRoID4gMzUwLF0KZ2dwbG90KG1lZFNlbGVjdCxhZXMod2lkdGgsTGVuZ3RoKSkgKyBnZW9tX3BvaW50KCkgCnBvbHkyID0gbG0oTGVuZ3RoIH4gcG9seSh3aWR0aCwyKSxkYXRhID0gbWVkU2VsZWN0KQpwb2x5MiAlPiUgc3VtbWFyeSgpCnBvbHkyICU+JSBwbG90KCkKYGBgCmBgYHtyfQptZWRTZWxlY3QgPSBtZWRbbWVkJHdpZHRoID4gMzUwLF0KZ2dwbG90KG1lZFNlbGVjdCxhZXMod2lkdGgsTGVuZ3RoKSkgKyBnZW9tX3BvaW50KCkgCnBvbHkzID0gbG0oTGVuZ3RoIH4gcG9seSh3aWR0aCwzKSxkYXRhID0gbWVkU2VsZWN0KQpwb2x5MyAlPiUgc3VtbWFyeSgpCnBvbHkzICU+JSBwbG90KCkKcG9seTMkcmVzaWR1YWxzICU+JSBsZXZlbmVUZXN0KG1lZFNlbGVjdCR3aWR0aCkKQUlDKHBvbHkxLHBvbHkyLHBvbHkzKQpgYGAKCgo=

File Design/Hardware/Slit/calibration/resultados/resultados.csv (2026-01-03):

 | Area | Mean | Min | Max | Angle | Length
1 | 154.240 | 245.888 | 138 | 255 | 90.000 | 192.000
2 | 149.120 | 254.146 | 176 | 255 | 90.000 | 185.600
3 | 108.160 | 249.521 | 151 | 255 | 90.000 | 134.400
4 | 178.560 | 253.534 | 152 | 255 | 90.000 | 222.400
5 | 210.560 | 253.757 | 189 | 255 | 90.000 | 262.400
6 | 165.120 | 250.810 | 179 | 255 | 90.000 | 205.600
7 | 163.200 | 227.984 | 105 | 255 | 90.000 | 203.200
8 | 232.319 | 254.656 | 196 | 255 | 90.000 | 289.600
9 | 132.480 | 248.995 | 148 | 255 | 90.000 | 164.800
10 | 122.240 | 251.529 | 124 | 255 | 90.000 | 152.000
11 | 204.160 | 252.119 | 158 | 255 | 90.000 | 254.400
12 | 181.120 | 253.880 | 196 | 255 | 90.000 | 225.600
13 | 144.000 | 237.747 | 137 | 255 | 91.023 | 179.228
14 | 119.680 | 250.364 | 126 | 255 | 90.000 | 148.800
15 | 183.680 | 253.178 | 176 | 255 | 90.000 | 228.800
16 | 158.080 | 251.781 | 173 | 255 | 90.000 | 196.800

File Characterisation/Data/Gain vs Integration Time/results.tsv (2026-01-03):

P1 | P2 | P3 | P4 | P5 | P6 | P7 | P8 | P9 | P10 | P11 | P12 | P13 | P14 | P15 | P16 | P17 | P18 | P19 | P20 | P21 | P22 | P23 | P24 | P25 | P26 | P27 | P28 | P29 | P30 | P31 | P32 | P33 | P34 | P35 | P36 | P37 | P38 | P39 | P40 | P41 | P42 | P43 | P44 | P45 | P46 | P47 | P48 | P49 | P50 | P51 | P52 | P53 | P54 | P55 | P56 | P57 | P58 | P59 | P60
11876.129333333334 | 11980.323999999999 | 12155.98888888889 | 12301.820444444445 | 12494.722222222223 | 12744.344444444445 | 13037.345777777777 | 13342.794666666668 | 13748.587555555554 | 14058.068888888889 | 14394.631111111114 | 14809.860444444445 | 15174.666666666666 | 15597.398666666666 | 16041.350666666665 | 16467.27511111111 | 16934.18355555556 | 17406.294222222223 | 17865.45688888889 | 18432.49644444444 | 18895.339555555554 | 19493.687111111107 | 19961.844444444447 | 20382.072444444442 | 20860.04844444445 | 21480.85911111111 | 22088.358666666667 | 22667.868444444444 | 23141.214666666667 | 23676.560888888886 | 24073.81777777778 | 24402.14311111111 | 24848.505777777777 | 25293.839555555554 | 25609.702666666668 | 25933.82177777778 | 26140.545777777774 | 26318.829777777777 | 26443.43422222222 | 26535.975111111107 | 26511.299555555557 |
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

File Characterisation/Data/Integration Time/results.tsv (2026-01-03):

P1 | P2 | P3 | P4 | P5 | P6 | P7 | P8 | P9 | P10 | P11 | P12 | P13 | P14 | P15 | P16 | P17 | P18 | P19 | P20 | P21 | P22 | P23 | P24 | P25 | P26 | P27 | P28 | P29 | P30 | P31 | P32 | P33 | P34 | P35 | P36 | P37 | P38 | P39 | P40 | P41 | P42 | P43 | P44 | P45 | P46 | P47 | P48 | P49 | P50 | P51 | P52 | P53 | P54 | P55 | P56 | P57 | P58 | P59 | P60
13676.773333333334 | 13813.029333333334 | 13810.643555555556 | 13862.663555555555 | 13869.622666666668 | 13994.223555555556 | 14143.105333333335 | 14361.655111111113 | 14538.776888888888 | 14740.165333333334 | 14995.815555555553 | 15246.567111111111 | 15491.87111111111 | 15802.184444444443 | 16087.918666666668 | 16367.375555555558 | 16661.041777777777 | 16932.80177777778 | 17233.896 | 17553.556000000004 | 17844.231555555554 | 18166.513333333332 | 18494.009777777777 | 18765.42177777778 | 18867.88311111111 | 19328.234222222225 | 19874.019555555555 | 20258.46088888889 | 20578.678666666667 | 20999.336444444445 | 21249.738222222222 | 21462.389777777782 | 21788.335555555557 | 22037.342666666667 | 22338.368444444444 | 22587.381333333335 | 22820.311999999998 | 23061.153333333335 | 23248.412444444442 | 23347.995999999996 | 23417.18888888889 |
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

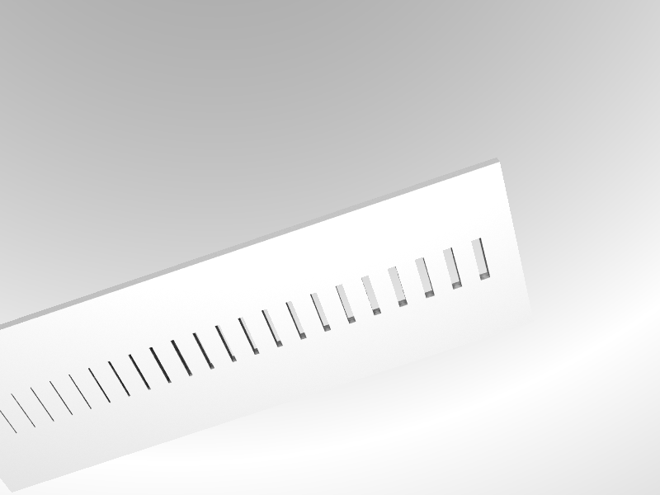
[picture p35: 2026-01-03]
Design/Hardware/Slit/test.png

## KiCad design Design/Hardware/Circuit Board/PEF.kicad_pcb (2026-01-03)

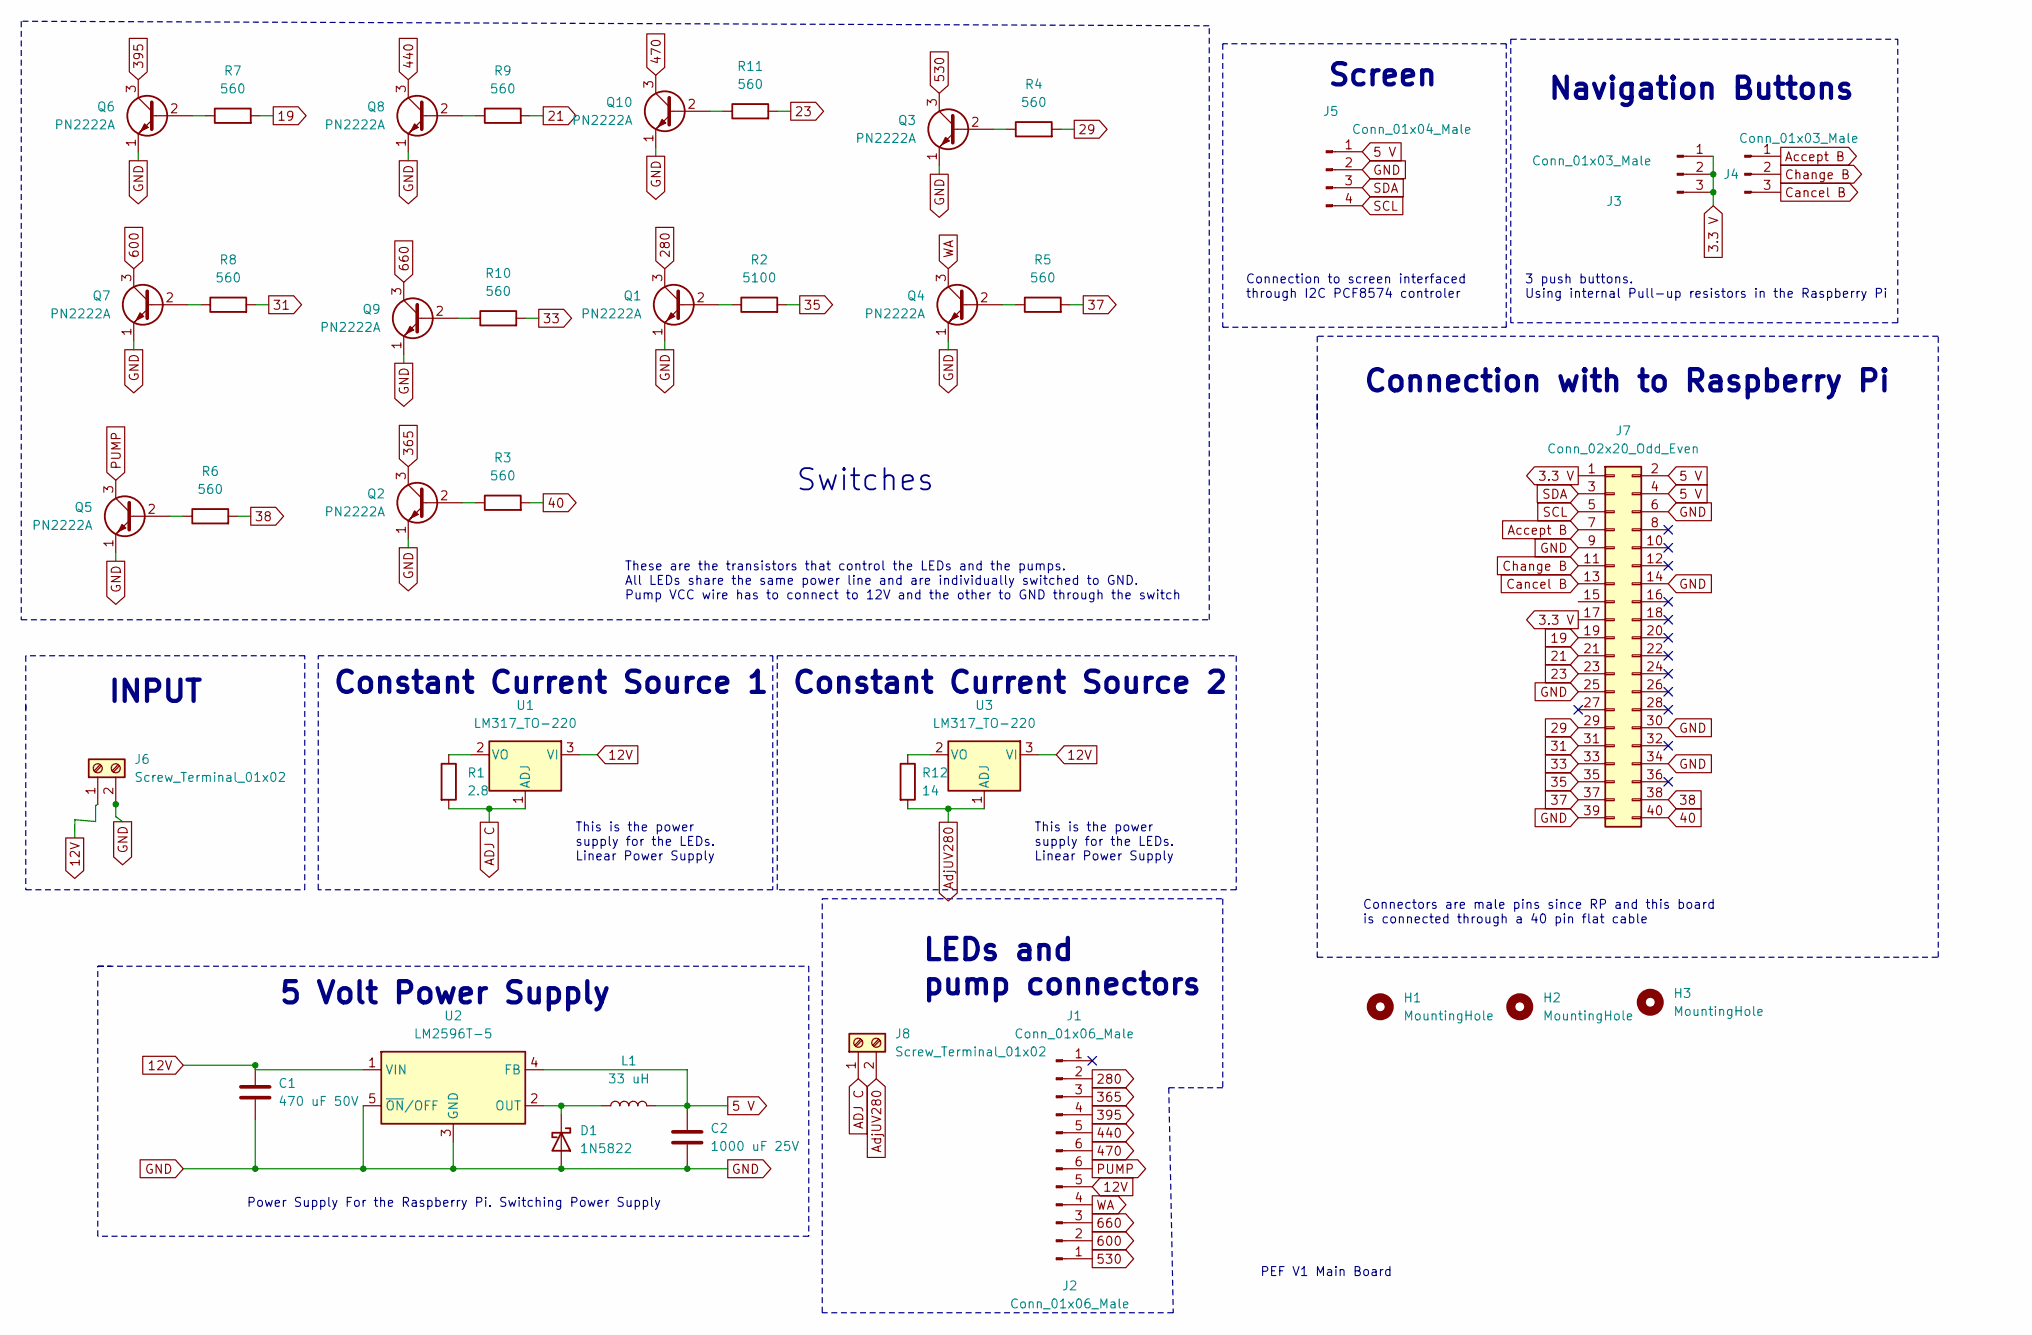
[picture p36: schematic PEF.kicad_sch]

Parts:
C1: 470 uF 50V; C_Radial_D10.0mm_H20.0mm_P5.00mm
C2: 1000 uF 25V; C_Radial_D8.0mm_H11.5mm_P3.50mm
D1: 1N5822; D_DO-201AD_P15.24mm_Horizontal
H1, H2, H3: MountingHole; MountingHole_5mm
J1, J2: Conn_01x06_Male; PhoenixContact_MSTBA_2,5_6-G-5,08_1x06_P5.08mm_Horizontal
J3, J4: Conn_01x03_Male; PinHeader_1x03_P2.54mm_Vertical
J5: Conn_01x04_Male; PinHeader_1x04_P2.54mm_Vertical
J6, J8: Screw_Terminal_01x02; TerminalBlock_Phoenix_MKDS-1,5-2_1x02_P5.00mm_Horizontal
J7: Conn_02x20_Odd_Even; PinHeader_2x20_P2.54mm_Vertical
L1: 33 uH; L_Radial_D7.2mm_P3.00mm_Murata_1700
Q1, Q2, Q3, Q4, Q5, Q6, Q7, Q8, Q9, Q10: PN2222A; TO-92_Inline
R1: 2.8; R_Axial_DIN0207_L6.3mm_D2.5mm_P10.16mm_Horizontal
R2: 5100; R_Axial_DIN0207_L6.3mm_D2.5mm_P10.16mm_Horizontal
R3, R4, R5, R6, R7, R8, R9, R10, R11: 560; R_Axial_DIN0207_L6.3mm_D2.5mm_P10.16mm_Horizontal
R12: 14; R_Axial_DIN0207_L6.3mm_D2.5mm_P10.16mm_Horizontal
U1, U3: LM317_TO-220; TO-220-3_Vertical
U2: LM2596T-5; TO-220-5_P3.4x3.7mm_StaggerOdd_Lead3.8mm_Vertical

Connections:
3.3 V: J3.1, J3.2, J3.3, J7.1, J7.17
5 V: C2.1, J5.1, J7.2, J7.4, L1.2, U2.4 (FB)
12V: C1.1, J2.5, J6.1, U1.3 (VI), U2.1 (VIN), U3.3 (VI)
19: J7.19, R7.2
21: J7.21, R9.2
23: J7.23, R11.2
29: J7.29, R4.2
31: J7.31, R8.2
33: J7.33, R10.2
35: J7.35, R2.2
37: J7.37, R5.2
38: J7.38, R6.2
40: J7.40, R3.2
280: J1.2, Q1.3 (C)
365: J1.3, Q2.3 (C)
395: J1.4, Q6.3 (C)
440: J1.5, Q8.3 (C)
470: J1.6, Q10.3 (C)
530: J2.1, Q3.3 (C)
600: J2.2, Q7.3 (C)
660: J2.3, Q9.3 (C)
ADJ C: J8.1, R1.2, U1.1 (ADJ)
Accept B: J4.1, J7.7
AdjUV280: J8.2, R12.2, U3.1 (ADJ)
Cancel B: J4.3, J7.13
Change B: J4.2, J7.11
GND: C1.2, C2.2, D1.2 (A), J5.2, J6.2, J7.6, J7.9, J7.14, J7.25, J7.30, J7.34, J7.39, Q1.1 (E), Q2.1 (E), Q3.1 (E), Q4.1 (E), Q5.1 (E), Q6.1 (E), Q7.1 (E), Q8.1 (E), Q9.1 (E), Q10.1 (E), U2.3 (GND), U2.5 (~ON/OFF)
unnamed: D1.1 (K), L1.1, U2.2 (OUT)
unnamed: Q1.2 (B), R2.1
unnamed: Q2.2 (B), R3.1
unnamed: Q3.2 (B), R4.1
unnamed: Q4.2 (B), R5.1
unnamed: Q5.2 (B), R6.1
unnamed: Q6.2 (B), R7.1
unnamed: Q7.2 (B), R8.1
unnamed: Q8.2 (B), R9.1
unnamed: Q9.2 (B), R10.1
unnamed: Q10.2 (B), R11.1
unnamed: R1.1, U1.2 (VO)
unnamed: R12.1, U3.2 (VO)
PUMP: J2.6, Q5.3 (C)
SCL: J5.4, J7.5
SDA: J5.3, J7.3
WA: J2.4, Q4.3 (C)

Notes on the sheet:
PEF V1 Main Board
Constant Current Source 1
LEDs and pump connectors
Connection with to Raspberry Pi
Power Supply For the Raspberry Pi. Switching Power Supply
5 Volt Power Supply
Constant Current Source 2
Screen
Connection to screen interfaced through I2C PCF8574 controler
3 push buttons. Using internal Pull-up resistors in the Raspberry Pi
INPUT
These are the transistors that control the LEDs and the pumps. All LEDs share the same power line and are individually switched to GND. Pump VCC wire has to connect to 12V and the other to GND through the switch
Connectors are male pins since RP and this board is connected through a 40 pin flat cable
Switches
Navigation Buttons
This is the power supply for the LEDs. Linear Power Supply

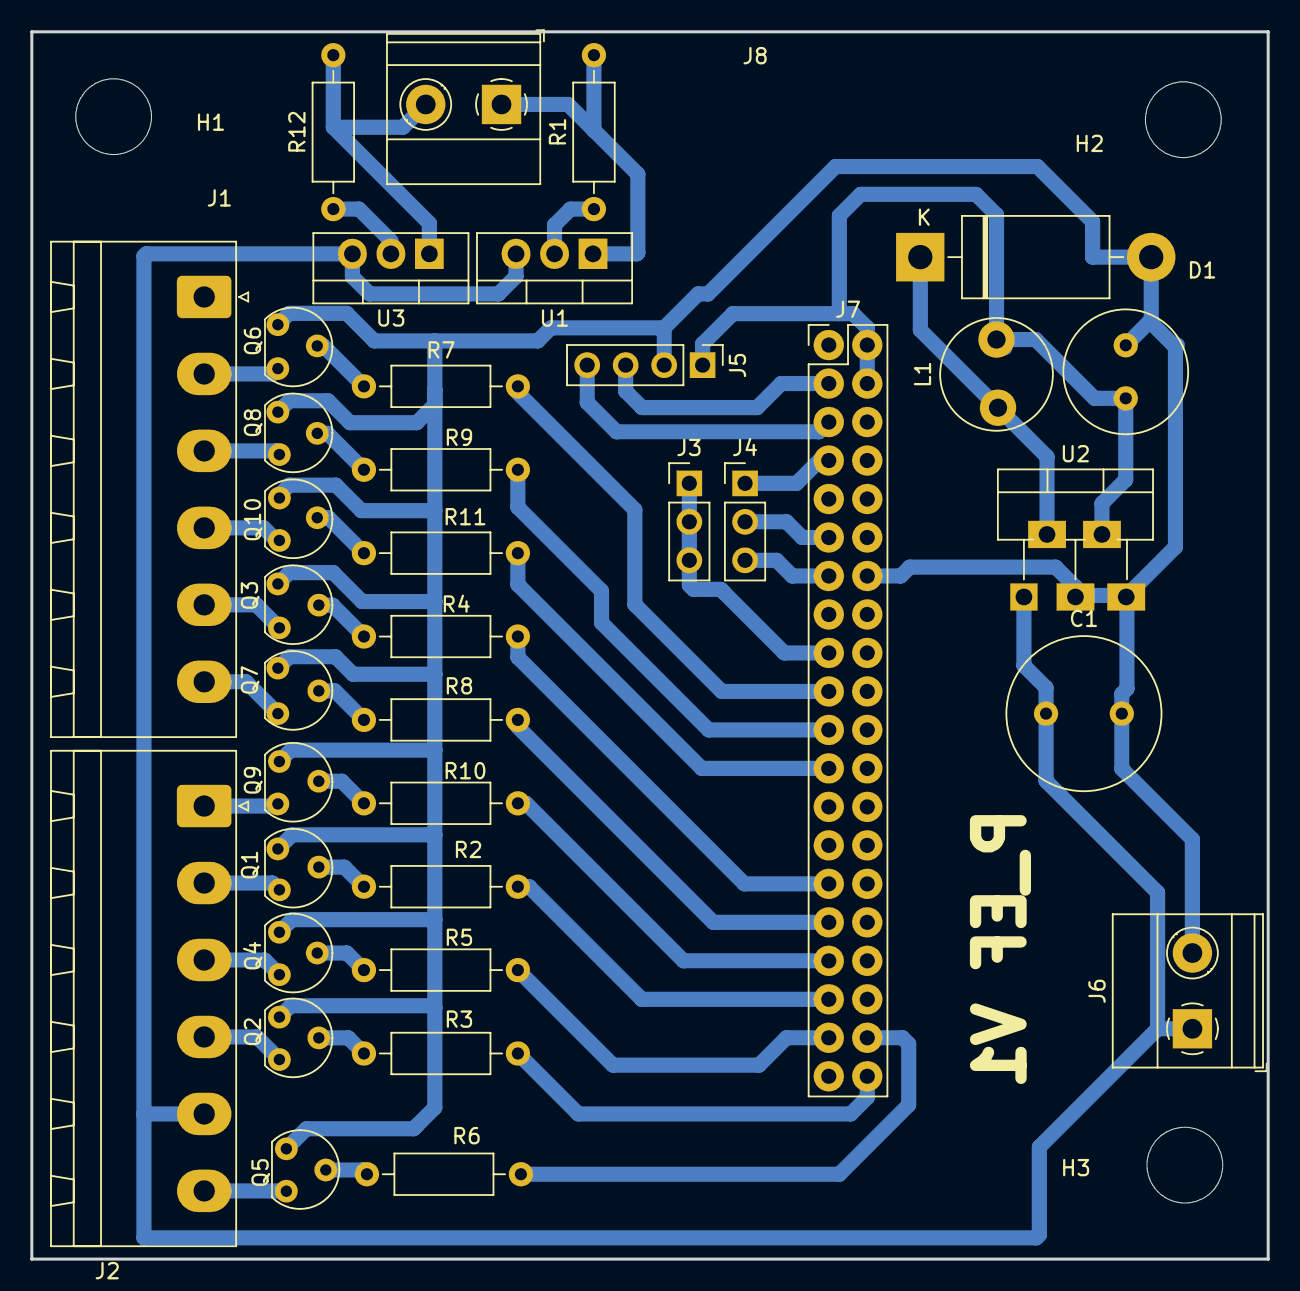
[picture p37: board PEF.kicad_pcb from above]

Board: 2 copper layers, 81.6 x 81.0 mm, 40 parts (0 on the bottom side), 44 nets.

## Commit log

2026-01-03 Initial commit: Complete Ecophysiometer files to build an Ecophysiometer (software, hardware and configuration files). Also, two implementation cases and characterisation experiments
    [BillOfMaterials.tsv, CALIBRATION TEST-Body.stl, CALIBRATION TEST.FCStd, Datos.ods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]
2026-01-05 Improving IR filter removal tutorial
